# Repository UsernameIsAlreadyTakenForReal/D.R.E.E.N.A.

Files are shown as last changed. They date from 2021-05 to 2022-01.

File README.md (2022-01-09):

# What is this?
Digital Recreation of Ejected Extremities, Namely Arms (D.R.E.E.N.A.)

A myoelectric robot hand, initially designed to be a prosthesis. Each finger is individually operated by a SG-90 servomotor. Wrist is not rotating.

This is my bachelor's degree project. As with all projects, it turned out way worse than I had expected; these kinds of projects require multiple iterations to get right, especially if you don't have experience with designing 3D objects that can actually be used. I only had one shot. Thanks, Eminem. I like how GitKraken looks, so I made a repo as well.

# If, for any reason, you want to get this working too...
which you shouldn't, since it requires a lot of stuff and there are easier projects to set up out there that work way, way better, here are some guides:

## *Pre- stuff that you need:*
- Blender or convertor for .blend files if you want to change the 3D models;
- A 3D printer. Project was printed with Ender 3 Pro, via software Ultimaker Cura 4.8.0, with PLA 1.75mm grey material, with 0.16mm step;
- Arduino IDE, really. Project was created with Visual Studio 2019 and vMicro;
- .blend files go big or go home. Need LFS: https://git-lfs.github.com/ 

## *For printing:*
For simpletons, each .STL file has to be printed ONCE. The palm is made up of three segments: the knuckles, the back of the hand and the knuckles. Thumb is one single object. Fingers are made up of two segments: proximal and distal. Distal has two segments, a _Body and a _Guard. 

1. Fingers:
   1. Index finger and Middle finger have the same Proximal model (the longest one);
   2. Index finger, Ring finger and Pinky finger have the same Distal model (_Body + _Guard);
   3. Ring finger has its own Proximal model (the middle-sized one);
   4. Pinky finger has its own Proximal model (the shortes one);
2. Thumb finger is the only one made up of one single segment, is a singular object, so that's fine. Thumb is referred to as 'thumb', not 'finger';
3. Palm + Wrist:
   1. Palm has Palm_Base and Palm_Interior; these two have little holes in them for magnets of ø 2mm;
   2. Knuckles were meant to be part of Palm_Interior, but due to it being impossible to print, they are now separated;
   3. Wrist is just an object, so that's fine. 

## *Components needed:*
Oh, boy...
1. Arduino Mega 2560 or any board with at least 5 PWM pins, 13 digital pins and 1 analog pin;
2. 1 myoelectric sensor. The code is written for a MyoWare AT-04-001;
3. 5 SG-90 servomotors;
4. 1 button to switch between function modes;
5. 1 4-digit 7-segment display;
6. Connectors (11 for the display, 3 for each servomotor, 3 for the myoelectric sensor, 3 for the button, 2 for the led;
7. 1 led;
8. Power supply for the servomotors;

Physical components...
1. Elastic string of at most ø 2mm (recommend ø 1.5mm);
2. Non-elastic string of at most ø 0.5mm;
3. 10 ø 2mm cylindric magnets.

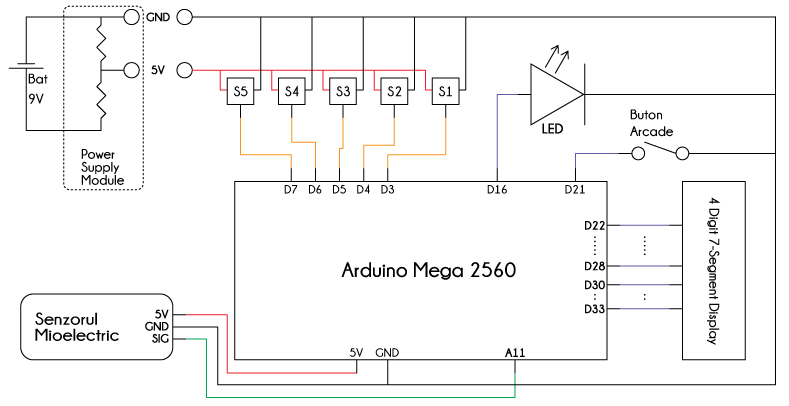
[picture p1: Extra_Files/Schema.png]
Note that servomotors are powered separately, though a 9V battery will not suffice. They need much, much more power


Note that servomotors are powered separately, though a 9V battery will not suffice. They need much, much more power.

## *For other wirings:*
Oh, boy 2.0... If you really made this this far and wish to continue (don't) please read everything before trying anything, and please test every component, electronic or not, before actually tying, knotting and glueing anything!
1. Run a non-elastic chord (like fishing strings) through the small hole in each finger; make a knot at the fingertip. The knot will be hidden by the _distal_guard_ segments;
2. Run an elastic chord through each finger's two big holes as to make an elongated elipsis that holds the finger together WITH the knuckles as well (knots!); by now you should have all 4 fingers attached to the knuckles and be able to pull the non-elastic chords to make the fingers flex;
3. Knuckles go into the small entrance of the Palm_Base segment; glue it if you want;
4. Servomotors go into the square-ish holes in the Palm_Base. Attach the shortest white extension; you will attach the non-elastic chord to it (tie it. Suffer like I suffered). Experiment with the 0 rotation of each that means finger is extended (since they are rotated IRL, their '0' rotation can be either 0 or 180 from the servo's view). For the motors associated with the pinky and ring finger you have to lay them on a side. To do this, you need to cut one wing off of each of these two motors. As for the layout, each motor can be placed in one way as to make the non-elastic chord take the shortest path;
5. Hope you have ø 2mm cylindric magnets lying around, 'cause you need them to hold Palm_Base and Palm_Interior together and still be able to open them up when needed;
6. Run a non-elastic chord and an elastic chord through the thumb and Palm_Interior; good luck at making that knot with the servo's white extension!;
7. Take all connectors from the servomotors out through the whole at the base of the palm. Add the wrist. And that's it.

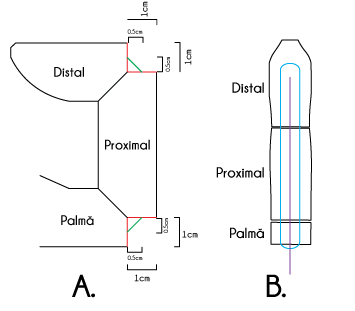
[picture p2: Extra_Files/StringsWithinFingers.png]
Blue for elastic chord. Purple for the non-elastic chord


Blue for elastic chord. Purple for the non-elastic chord.

## *For understanding the project:*
There are 2 modes of operation: with predefined grips and free mode (which works like sh*t). There are 4 groups of predefined grips, each with 2 grips:
1. Basic
   1. Fist
   2. Grip
2. Pinches
   1. Pinch
   2. PinchNoFingers
3. Tripods
   1. Tripod
   2. TripodNoFingers
4. Extra (programmable)
   1. RockOn
   2. Extra2 

The button has these possible functions, based on pressing length and number of presses:
1. rapid (<1 sec) | 1 press   - change grip mode (two grip modes in a group)
2. rapid (<1 sec) | 2 presses - next grip group
3. slow (1 - 3 sec) | 1 press - lock servos
4. v slow (3-5 sec) | 1 press - change op mode (predefined / free mode)
5. vv slow (>5 sec) | 1 press - shut down

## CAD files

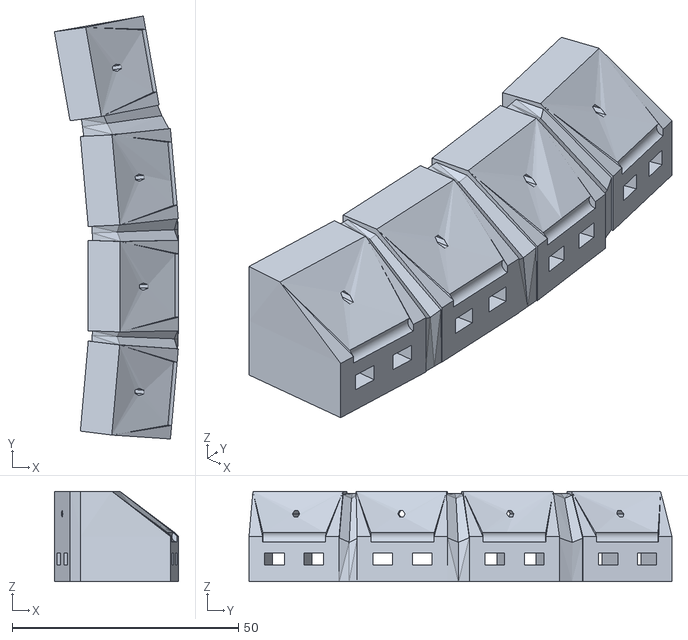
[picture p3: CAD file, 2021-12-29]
STL_Files/Knuckles.stl
27.5 x 93.5 x 20.0

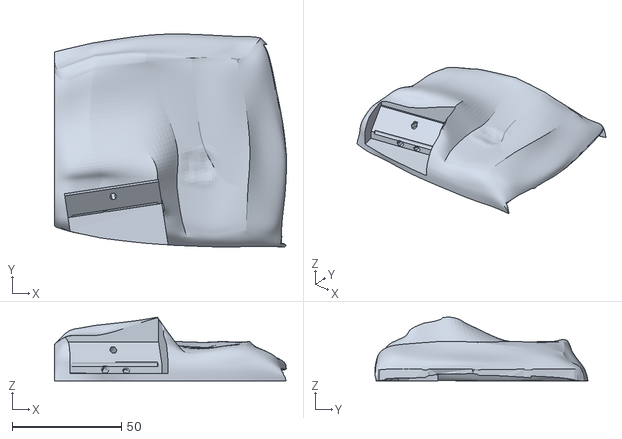
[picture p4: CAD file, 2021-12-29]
STL_Files/Palm_Interior.stl
105.9 x 97.3 x 29.1

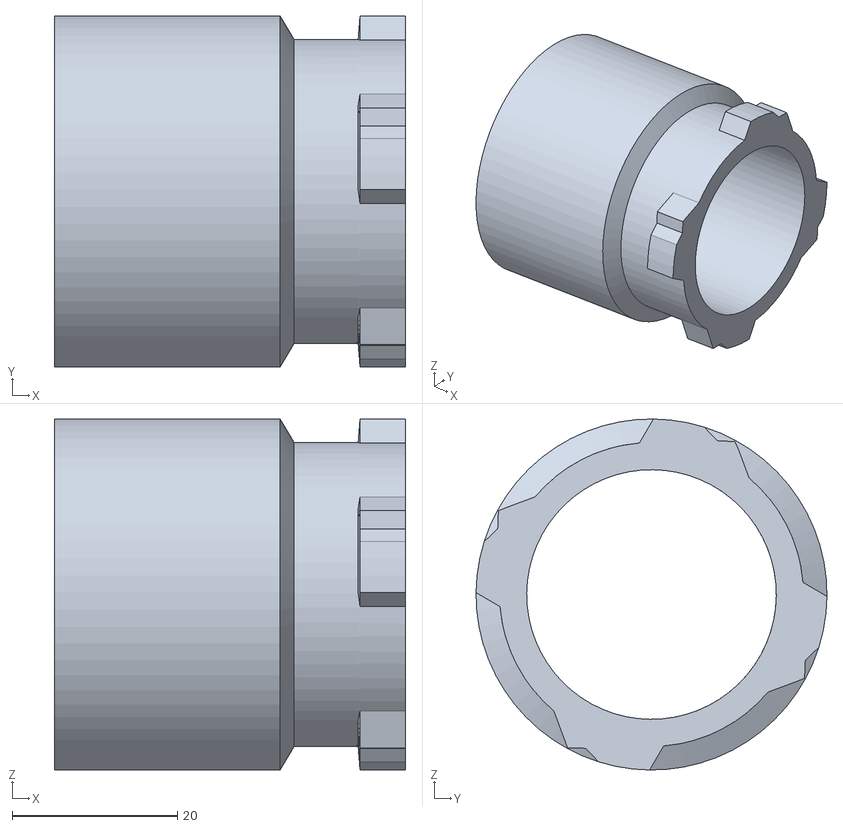
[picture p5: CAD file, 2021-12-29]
STL_Files/Wrist.stl
42.5 x 42.5 x 42.5

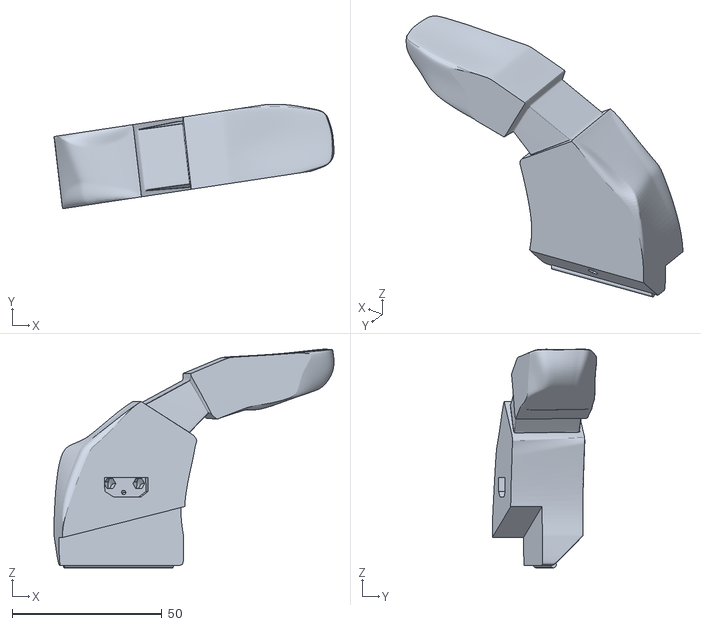
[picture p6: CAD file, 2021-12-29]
STL_Files/Thumb.stl
93.5 x 34.9 x 73.0

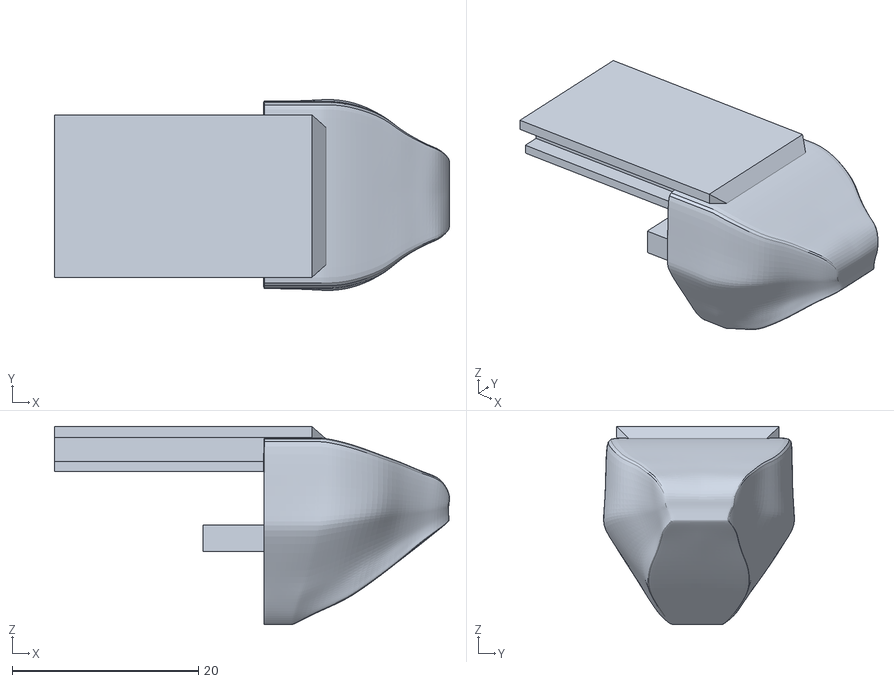
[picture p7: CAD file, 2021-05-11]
STL_Files/Middle_Distal_Guard.stl
42.4 x 20.5 x 21.2

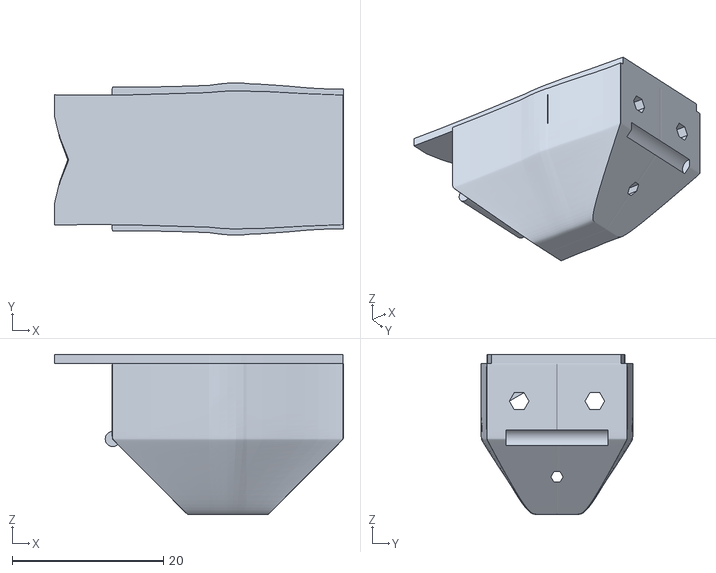
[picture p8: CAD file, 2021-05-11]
STL_Files/Pinky_Proximal.stl
38.2 x 20.1 x 21.2

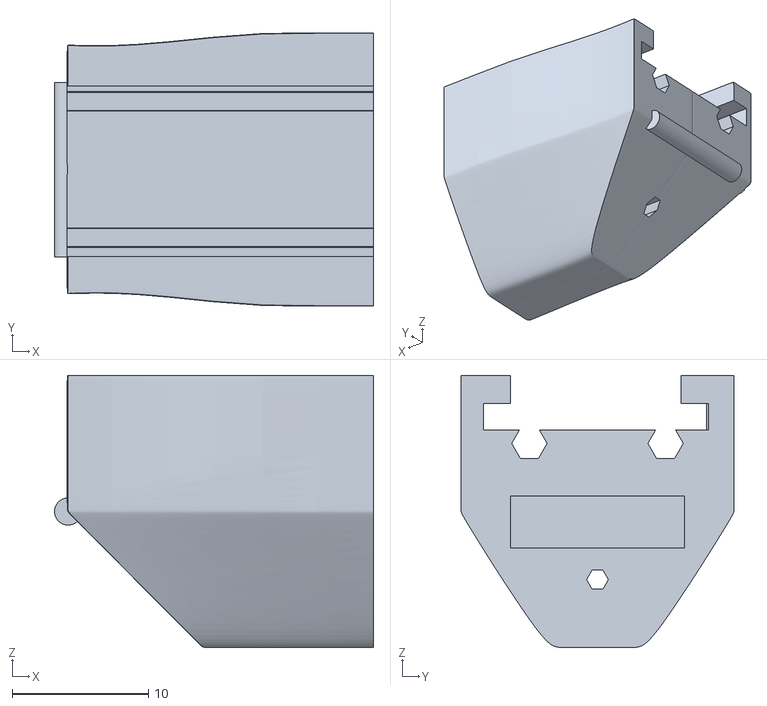
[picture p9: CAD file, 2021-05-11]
STL_Files/Middle_Distal_Body.stl
23.4 x 20.1 x 20.0

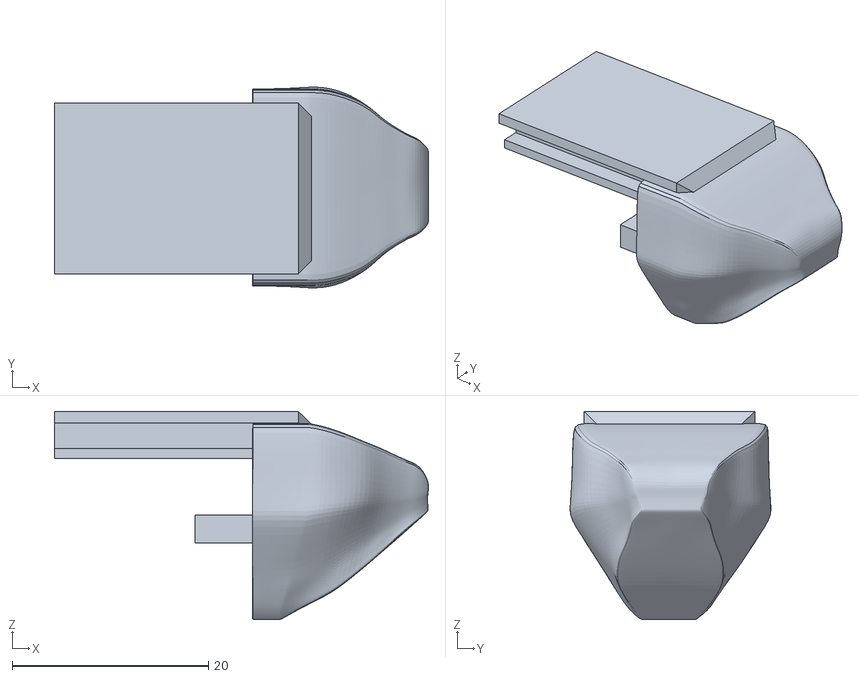
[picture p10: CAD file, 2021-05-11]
STL_Files/Ring_Distal_Guard.stl
38.1 x 20.5 x 21.2

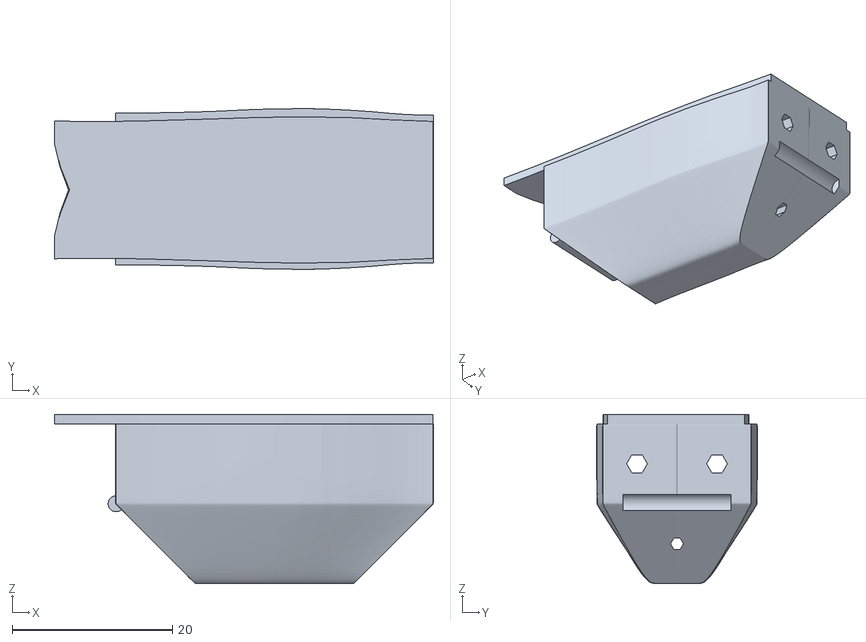
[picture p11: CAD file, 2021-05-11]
STL_Files/Ring_Proximal.stl
47.4 x 20.1 x 21.2

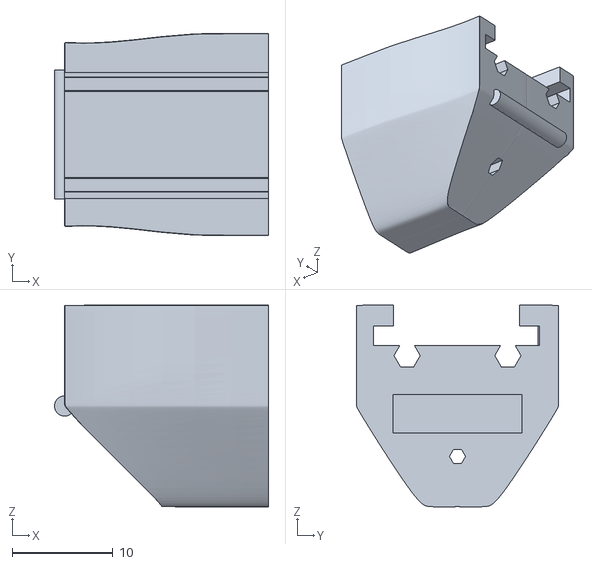
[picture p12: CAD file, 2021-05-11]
STL_Files/Ring_Distal_Body.stl
21.2 x 20.1 x 20.0

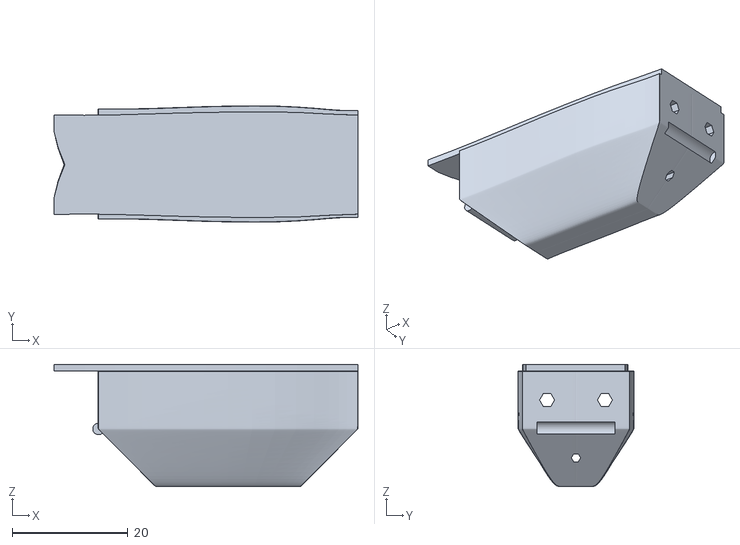
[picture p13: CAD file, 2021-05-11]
STL_Files/Middle_Proximal.stl
52.6 x 20.1 x 21.2

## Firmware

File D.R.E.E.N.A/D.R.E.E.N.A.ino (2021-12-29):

// Author: Cislianu Radu 
// Project: Myoelectric prosthesis || Digital Recreation of Ejected Extremities, Namely Arms (D.R.E.E.N.A.)

#include "Definitions.h"
#include <Servo.h>
#include <avr/sleep.h>

#define Btn_1 9
#define Btn_2 21

#define LEDTemp 16
#define servoDelay 5
#define slowServoDelay 15
#define maxIddleTime 2000

#define sensorThreshold 2.5
#define sensorPin A11 
#define sensorDelay 5   // so we do not overload the pin and the sensor. The point to make here is that we want to read the sensor at all times
                        // so that means inside the loop() function, yet we should delay it by this amount so we don't overload. At the time of
                        // writing this, no test has yet been undergone and I cannot say for sure if it will interfere with the button and dis-
                        // play functions. Let's hope not

// using SG90 servos, wiring is as follows:
// Red:    VCC    (+)
// Brown:  Ground (-)
// Orange: PWM	  (!)
// The Servo objects for each finger
Servo thumb;
Servo index;
Servo middle;
Servo ring;
Servo pinky;
bool are_servers_locked = false;

int angle = 0;
int futemasPeEl;

// used in calculating the amount of time and number of times the button has been pressed
int button_state = 1;
int last_button_state = 1;
int press_start = 2147483647;
int press_stop = 2147483647; // MAX_INT to avoid having the program think there has been a very long button press when the button is pressed by the user for the first time. 
int press_time;
int iddle_time;
int previous_time = 0; // 1 - short press, 2 - long press
bool short_time = false;
bool button_action_needs_consumption = false;
int press_counter = 0;
int aux_timer_1;

// EXTRA stuff
int sensor_state = 0;
int sensor_last_state = 0;
bool system_firing = false;
int led_time = 0;

// operating modes
opMode currentMode = opMode::grips;
freeModes currentFree = freeModes::noThumb; 
gripModes currentGrip = gripModes::fist;
gripGroups currentGroup = gripGroups::basic;
bool isConfigMode = false;

// CONFIG MODE state
int config_state;
int flex_vector_ext1[5] = { 0, 0, 1, 1, 0 };
int flex_vector_ext2[5] = { 0, 1, 0, 1, 1 };
int edit_index = 0;

// used in Display Interruptions (Battery level and Locking Servos)
int display_interruption_start_time;
int display_interruption_type; // 0 - none, 1 - battery, 2 - lock
int aux_timer_2;

// At last, the sensor itself
int sensor_value;           // for analogRead()
float voltage;              // to get an actual value that makes sense

// The setup() function runs once each time the micro-controller starts
void setup()
{
    Serial.begin(9600);

    Serial.println("\n\n!!New session!!");

    // Attaching the pins to each servo 
    thumb.attach(servoThumbPin);
    index.attach(servoIndexPin);
    middle.attach(servoMiddlePin);
    ring.attach(servoRingPin);
    pinky.attach(servoPinkyPin);

    // Moving each servo to its 0 position
    thumb.write(thumbMinAngle);
    index.write(indexMinAngle);
    middle.write(middleMinAngle);
    ring.write(ringMinAngle);
    pinky.write(pinkyMinAngle);


    thumb.detach();
    index.detach();
    middle.detach();
    ring.detach();
    pinky.detach();

    pinMode(Btn_1, INPUT);
    pinMode(Btn_2, INPUT_PULLUP);

    pinMode(disD1, OUTPUT);
    pinMode(disD2, OUTPUT);
    pinMode(disD3, OUTPUT);
    pinMode(disD4, OUTPUT);
    pinMode(disP1, OUTPUT);
    pinMode(disP1, OUTPUT);
    pinMode(disP2, OUTPUT);
    pinMode(disP3, OUTPUT);
    pinMode(disP4, OUTPUT);
    pinMode(disP5, OUTPUT);
    pinMode(disP6, OUTPUT);
    pinMode(disP7, OUTPUT);

    pinMode(LEDTemp, OUTPUT);

    // Testing servos when reseting
    /*FlexThumb();
    delay(500);
    ExtendThumb();
    delay(500);

    FlexIndex();
    delay(500);
    ExtendIndex();
    delay(500);

    FlexMiddle();
    delay(500);
    ExtendMiddle();
    delay(500);

    FlexRing();
    delay(500);
    ExtendRing();
    delay(500);

    FlexPinky();
    delay(500);
    ExtendPinky();
    delay(1000);*/

    //digitalWrite(LEDTemp, LOW);
}

// Loop() function, this bit of code runs forever on the board
void loop()
{
    //////////////// Test code ////////////////
    // 
    ////////////////// Good code ////////////////

    if (isConfigMode == false) {

        //// Temp -- will be replaced with the sensor variant
        //sensor_state = digitalRead(Btn_1);

        sensor_value = analogRead(sensorPin);
        voltage = sensor_value * (5.0 / 1023.0);

        Serial.println(voltage);

        if (voltage > sensorThreshold) {
            sensor_state = 1;
        }

        else {
            sensor_state = 0;
        }

        if (button_action_needs_consumption == true && sensor_state == 1) {

            display_interruption_type = 3;
            display_interruption_start_time = millis();
            button_action_needs_consumption = false;
        }



        if (sensor_state != sensor_last_state) {

            if (sensor_state == 1) {

                if (system_firing == false) {

                    system_firing = true;
                    Serial.println("On");

                    if (are_servers_locked == false) {
                        if (currentMode == opMode::grips)
                            FlexFingersWithGrip();
                    }
                }

                else {

                    system_firing = false;
                    Serial.println("Off");

                    if (are_servers_locked == false) {
                        if (currentMode == opMode::grips)
                            ExtendFingersWithGrip();
                    }
                }
            }
        }

        sensor_last_state = sensor_state;

        // Free mode rotations
        if (are_servers_locked == false) {
            if (currentMode == opMode::freeMovement) {

                if (system_firing == true && sensor_state == 1) { // if the button is pressed and "ON" || if the sensor senses signal and �ON�

                    if (angle < 180) {
                        angle++;


                        if (angle < indexMaxAngle) {
                            index.write(angle);
                        }

                        if (middleMinAngle - angle >= middleMaxAngle) {
                            middle.write(middleMinAngle - angle);
                        }

                        if (angle < ringMaxAngle) {
                            ring.write(angle);
                        }

                        if (pinkyMinAngle - angle >= pinkyMaxAngle) {
                            pinky.write(pinkyMinAngle - angle);
                        }

                        if (currentFree == freeModes::withThumb) {

                            if (angle < thumbMaxAngle) {
                                thumb.write(angle);
                            }
                        }
                        delay(slowServoDelay);
                    }

                }

                if (system_firing == false && sensor_state == 1) { // if the button is pressed and "OFF"

                    if (angle > 0) {
                        angle--;

                        if (angle > indexMinAngle) {
                            index.write(angle);
                        }

                        if (middleMinAngle - angle >= middleMaxAngle) {
                            middle.write(middleMinAngle - angle);
                        }

                        if (angle > ringMinAngle) {
                            ring.write(angle);
                        }

                        if (pinkyMinAngle - angle >= pinkyMaxAngle) {
                            pinky.write(pinkyMinAngle - angle);
                        }

                        if (currentFree == freeModes::withThumb) {
                            if (angle > thumbMinAngle) {
                                thumb.write(angle);
                            }
                        }
                        delay(slowServoDelay);
                    }
                }
            }
        }

        // this has to keep the display alive (since we use more than 1 letter)
        // for the "interrupting" displays (L o c 0 / L o c 1 || c o n F) I will have a bool "NeedsDisplayInterrupt" that, if on true, will go
        // on to display the 2x2 possible thingies, and when the timer (i.e. millis() - interrupting_display_time_start) goes beyond 2 seconds, bool goes false
        if (display_interruption_type == 0) {

            if (currentMode == opMode::freeMovement) {
                UpdateDisplayFree();
            }

            if (currentMode == opMode::grips) {
                UpdateDisplayGrips();
            }
        }

        // if there is any kind of display interruption, we will display it accordignly
        if (display_interruption_type != 0) {
            DisplayInterrupt();
            aux_timer_2 = millis() - display_interruption_start_time;
            if (aux_timer_2 > 2000) {

                if (display_interruption_type == 3) {
                    display_interruption_type = 0;
                    isConfigMode = true;
                    config_state = 1;
                    DisplayClear();
                }

                else {
                    display_interruption_type = 0;
                }

            }
        }

        // Due to the nature of the Arcade button, and using INPUT_PULLUP for it to work, when not pressed, digitalRead(Btn_2) will return HIGH;
        // we take the current state
        button_state = digitalRead(Btn_2);

        if (button_state != last_button_state) {    // if it has changed
            UpdateButtonState();                    // fire the function
        }

        // then this piece of magic
        last_button_state = button_state;

        // since we can call millis() very quickly here, we can establish now if only one button was pressed
        if (short_time == false) {
            if (button_action_needs_consumption == true) {
                aux_timer_1 = millis() - press_stop;
                if (aux_timer_1 > maxIddleTime) {

                    Serial.print("millis() - press_stop: "); Serial.print(aux_timer_1); Serial.print("\n");
                    TreatButtonAction();
                }
            }
        }

        // Flickering light once each second to know that a second has passed
        if (button_state == LOW) {
            led_time = millis() - press_start;

            if (led_time > 950 && led_time < 1050) {

                digitalWrite(LEDTemp, LOW);
                delay(10);
                digitalWrite(LEDTemp, HIGH);

            }

            if (led_time > 1950 && led_time < 2050) {

                digitalWrite(LEDTemp, LOW);
                delay(10);
                digitalWrite(LEDTemp, HIGH);
            }

            if (led_time > 2950 && led_time < 3050) {

                digitalWrite(LEDTemp, LOW);
                delay(10);
                digitalWrite(LEDTemp, HIGH);
            }

            if (led_time > 3950 && led_time < 4050) {

                digitalWrite(LEDTemp, LOW);
                delay(10);
                digitalWrite(LEDTemp, HIGH);
            }

            if (led_time > 4950 && led_time < 5050) {

                digitalWrite(LEDTemp, LOW);
                delay(10);
                digitalWrite(LEDTemp, HIGH);
            }
        }

        delay(sensorDelay);
    }

    else if (isConfigMode == true) {

        button_state = digitalRead(Btn_2);

        if (button_state != last_button_state) {    // if it has changed
            UpdateButtonStateCONFIG();                    // fire the function
        }

        // then this piece of magic
        last_button_state = button_state;


        UpdateDisplayCONFIG();

        // Flickering light once each second to know that a second has passed
        if (button_state == LOW) {
            led_time = millis() - press_start;

            if (led_time > 950 && led_time < 1050) {
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

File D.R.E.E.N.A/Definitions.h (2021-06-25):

#ifndef _Definitions_h
#define _Definitions_h


//#include "References.h"	// this could have worked, but when moving the project out of C:/ (Arduino libraries are located in C:/), 
							// the compiler doesn't find Servo.h if it's not #included in the main .ino file

#include <Servo.h>

// Arduino pins for each servo PWM pin. This is the only Servo pin directly connected to the Arduino. Servos should be powered separately (i.e. using a 9V battery)
#define servoThumbPin 3
#define servoIndexPin 4
#define servoMiddlePin 5
#define servoRingPin 6
#define servoPinkyPin 7

// some servos don't need to go all the way and should be ajusted through testing
// also, due to placement, the servos for the Middle and Pinky finger have to rotate in the opposite direction for them to pull the finger
#define pinkyMaxAngle 0
#define ringMaxAngle 180
#define middleMaxAngle 0 
#define indexMaxAngle 180
#define thumbMaxAngle 180

#define pinkyMinAngle 180
#define ringMinAngle 0
#define middleMinAngle 180
#define indexMinAngle 0
#define thumbMinAngle 0

// Pins for the 4 Digit 7-Segment Display. D1-D4 control which Digit is changed (to select a certain digit, put its D pin on LOW!)
//		  P1
//		 ____ 
//	 P6	|    | P2
//		|_P7_| 
//	 P5 |    | P3
//		|____|
//		  P4
#define disP1 22
#define disP2 23
#define disP3 24
#define disP4 25
#define disP5 26
#define disP6 27
#define disP7 28
#define disD1 30
#define disD2 31
#define disD3 32
#define disD4 33


///////////// Groups Definitions /////////////

enum opMode {
	grips,
	freeMovement
};

enum freeModes {
	withThumb,
	noThumb
};

// since we control each finger individually, we should define multiple ways of closing the fingers
// fist - fingers first, then thumb
// grip - fingers only
// pinch - thumb, then index |
// tripod - thumb, then index + middle | 
// extra1 - peace among worlds
// extra2 - \m/, just because we have a servo on the pinky
enum gripModes {
	fist,
	grip,
	pinch,
	pinchNoFingers,
	tripod,
	tripodNoFingers,
	extra1,
	extra2
};

enum gripGroups {
	basic,
	pinches,
	tripods,
	extraGrips
};

// Defining ++ and -- operations for gripGroups, since it will be easier to use this instead of a switch() when user sends input 
// Also implementing here because I couldn't get it to work inside Definitions.cpp for whatever reason
inline gripGroups& operator++ (gripGroups& m) { // ++
	return m = (m == gripGroups::extraGrips) ? gripGroups::basic : static_cast<gripGroups>(static_cast<int>(m) + 1);
}
inline gripGroups& operator-- (gripGroups& m) { // --
	return m = (m == gripGroups::basic) ? gripGroups::extraGrips : static_cast<gripGroups>(static_cast<int>(m) - 1);
}
inline opMode& operator++ (opMode& m) {
	return m = (m == opMode::freeMovement) ? opMode::grips : static_cast<opMode>(static_cast<int>(m) + 1);
}



//////////// Function Definitions ////////////
////////////// for NORMAL modey //////////////

// Button actions
void TreatButtonAction();
void UpdateButtonState();
void ChangeGripMode();
void UpdateGripMode();
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

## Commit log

2021-05-11 Up-To-Date kind of commit. Like migrating to GitHub. Take this, Danut. Also happy birthday!
    [Index&Ring&Pinky_Distal_Body.blend, Index&Ring&Pinky_Distal_Guard.blend, Index_Distal_Body.stl, Index_Distal_Guard.stl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]
2021-05-13 6cm No Problem for War
    Don't you understand that there's no problem for war?
2021-05-13 6cm No Problem for War, including corners of Palm_Base
2021-05-13 Did not apply modifiers, but Palm_Interior is now cut. Also extra pins and magnets.
    Also lowered the thumb servo
2021-05-14 Working on Motor_Bands
2021-05-15 Changed tube for Thumb_FishingLine. Pre-modifying of the Thumb commit
2021-05-15 First stages of the tip of the thumb
2021-05-15 Smth like that but less like Razvan's fingers
2021-05-21 Almost done. Need to consult with Adi for printing
2021-05-21 New Ideas. Also made 1 Knuckle. TODO: Print _Base vertically!
2021-05-26 Stand Motors
2021-05-28 Added Arm just for the fuck of it
    [Arm.blend]
2021-05-30 Fin la print
2021-06-07 Moved the Arduino vMicro project into D:/, so it should be portable now
    Button: how long has been pressed + changes grip mode.
2021-06-07 First push following the instalation of LFS
    [Arm.blend, Index&Ring&Pinky_Distal_Body.blend, Index&Ring&Pinky_Distal_Guard.blend, Middle&Index_Proximal.blend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]
2021-06-08 Arcade button works now. 4 digit 7 segment display works aswell.
    Need to check battery level, and treat the lock on/off stuff.
2021-06-09 Free and Grip operationModes work. Display works correctly, so does the button. Implemented motor action, but needs further improvement
2021-06-12 Well, technically it is complete. Locking servos and shutdown is the last thing. Good luck with that
2021-06-12 Well, locking servos works now. How about shutdown?
2021-06-16 Installed Blender 2.93, did some further failsafe-ing in the code.
    Commit before changing the variable name
    [Palm_36.blend]
2021-06-17 Sleep mode is written. WHY THE FUCK IS THE LED LIGHTING???????
2021-06-22 Sleep mode is updated. STILL, WHY THE FUCK THE LED LIGHT?
2021-06-22 Fixed LED... ffs
2021-06-25 This time, commiting the CONF mode... and the way servos work with their vectors... ffs...
2021-06-28 Attach + Detach each time. Fixes some of the servo spinning
    [Palm_36.blend]
2021-12-29 Repo clean-up 1
    [Ring_Proximal.stl, Thumb.stl, Wrist.stl]
2021-12-29 Repo clean-up 2
    [Index_Proximal.stl, Knuckles.stl, Middle_Distal_Body.stl, Middle_Distal_Guard.stl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]
2021-12-29 Repo clean-up 3
    [Index&Ring&Pinky_Distal_Body.blend, Index&Ring&Pinky_Distal_Guard.blend, Index_Distal_Body.stl, Index_Distal_Guard.stl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]
2021-12-29 Repo clean-up 5
    [Arm.blend, Index&Ring&Pinky_Distal_Body.blend, Index&Ring&Pinky_Distal_Guard.blend, Index_Distal_Body.stl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]
